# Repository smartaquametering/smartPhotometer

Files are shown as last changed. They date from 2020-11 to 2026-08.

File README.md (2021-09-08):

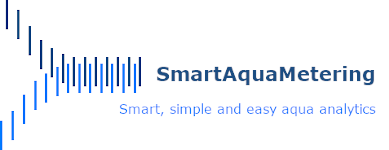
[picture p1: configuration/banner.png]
Banner


# smartPhotoMeter, smartColoriMeter and smartSpectroMeter

Easy-to-use OpenSource devices for **measurement of transmission, emission and absorption of light** at given ranges of wavelengths of colored or not colored substances in solution.

- For analytics of aqueous solutions.
- Works with ultraviolet, visible and near infrared light ranges, by wavelengths around 320 up to 950 nm.

Allows **CIE compliant measurements of colors** and their transformation into various color spaces and color systems including the determination of **colour differences to common color indices/references** according to classic as well as modern standards (ΔE CIE 1976, ΔE CIE 1994, ΔE CIE 2000, ΔE CMC(1:1), ΔE CMC(2:1), ΔE DIN99).

**Turbidity – a source of error**</br>
The turbidity of a sample is often underestimated, because often it is not possible to see it visually.</br>
**The nephelometric turbidity of a sample is measured and displayed for every single measurement automatically.**

Due to their wide range of application, their reliability and robustness

<table>
<tr>
  <td>
  <td>Transmission
  <td>Emission
  <td>Absorbance
  <td>Colorimetric</br>analysis
  <td>Spectral</br>analysis
  <td>Nephelometric</br>turbidity
</tr>
<tr>
  <td><b>smartPhotoMeter</b>
  <td align="center">X
  <td align="center">
  <td align="center">X
  <td align="center">
  <td align="center">
  <td align="center">X
</tr>
<tr>
  <td><b>smartTurbidiMeter</b>
  <td align="center">X
  <td align="center">
  <td align="center">X
  <td align="center">
  <td align="center">
  <td align="center">X
</tr>
<tr>
  <td><b>smartColoriMeter</b>
  <td align="center">
  <td align="center">
  <td align="center">
  <td align="center">X
  <td align="center">
  <td align="center">
</tr>
<tr>
  <td><b>smartSpectroMeter</b>
  <td align="center">X
  <td align="center">X
  <td align="center">X
  <td align="center">X
  <td align="center">X
  <td align="center">X
</tr>
</table>

they **can be perfectly used as portable analytical instruments for outdoor analytics**.

**Your insurance for secure measurement results.**

## Electromagnetic radiation used for photometric and spectrum analysis

In simple terms, photometry is a measurement method for determining the concentration of colored solutions with the aid of electromagnetic radiation (“light”).

The two most common types of photometers are:

- Spectrophotometer
- Filter photometer

In spectrophotometers a monochromator (with prism or with grating) is used to obtain monochromatic light of defined wavelengths. They can also be used to scan the spectrum of the absorbing substance.
Spectrum scans can be used for additional colorimetric analysis at a wavelength range from 360 nm to 830 nm.

In filter photometers, optical filters are used to give the monochromatic light.

### smartPhotoMeter

Due to the evolution and availability of **various types of LEDs** it is easily possible **to obtain nearly monochromatic light with specific wavelength ranges** for respective measurements, but without the need to setup an complex and sensitive monochromator or filter mechanismn.

- The selection of the optimum wavelength range depends on the color of the sample solution and the associated absorption of the complementary color.
- For a blue solution, a wavelength range near to yellow should be used (green LED), while for a yellow solution a blue LED should be used, since always the complementary color is absorbed.
- The more closely the absorption maximum of the substance to be detected is approached, the higher the performance of the photometer will be.
- The smaller the spectral bandwidth of the LED (the range between lower and upper wavelength), the higher the photometer resolution.

### smartTurbidiMeter

The photometric determination of turbidity at a wavelength of 850 nm only to circumvent additional absorption of color in the visible region (following DIN EN ISO 7027).

- Double-beam measurement by using two independant IR light sources and optical paths

### smartColoriMeter

An RGB sensor with **color sensing photodiodes** (red, green, blue) can be used **for colorimetric analysis**.

An IR blocking filter, integrated on-chip and localized to the color sensing photodiodes, minimizes the IR spectral component of the incoming light and allows color measurements to be made accurately.

### smartSpectroMeter

Due to the evolution and availability of **various types of spectral sensors** it is easily possible **to measure the intensity of light at a specific wavelength range**, but without the need to setup an complex and sensitive monochromator or filter mechanismn.

By using a low-voltage **quartz halogen capsule lamp** (Quartz-UV Open) and an **array of spectral sensors** a spectrum for the range of UVA, VIS and IR-A light can be obtained accurately.

These spectral sensors have **20 independent on-device optical filters** whose spectral response is defined in a range **from 330 nm to 940 nm** with a Full Width Half
Max (FWHM) of 20 nm.

Spectrum scans can be used **for qualitative, quantitative and colorimetric analysis** at a wavelength range from 360 nm to 830 nm.

### Cuvette

The selection of an appropriate cuvette for each measurement is crucial. The material (depending on the wavelength) and size of the cuvette are the two key factors.

- High-quality materials such as quartz are used in rectangular standard cuvettes for measurements in the UV range.
- In addition to round and rectangular cuvettes, there are also special cuvettes, such as flow-through cuvettes, where the sample solution is passed into and out of the cuvette by a pump.
- The size of the cuvette is directly related to the layer thickness that is effective in the Lambert-Beer law. Generally speaking, the larger the cuvette and the sample volume, the greater the layer thickness, and the more sensitive the measurement can be.

### Setup options

<table>
<tr>
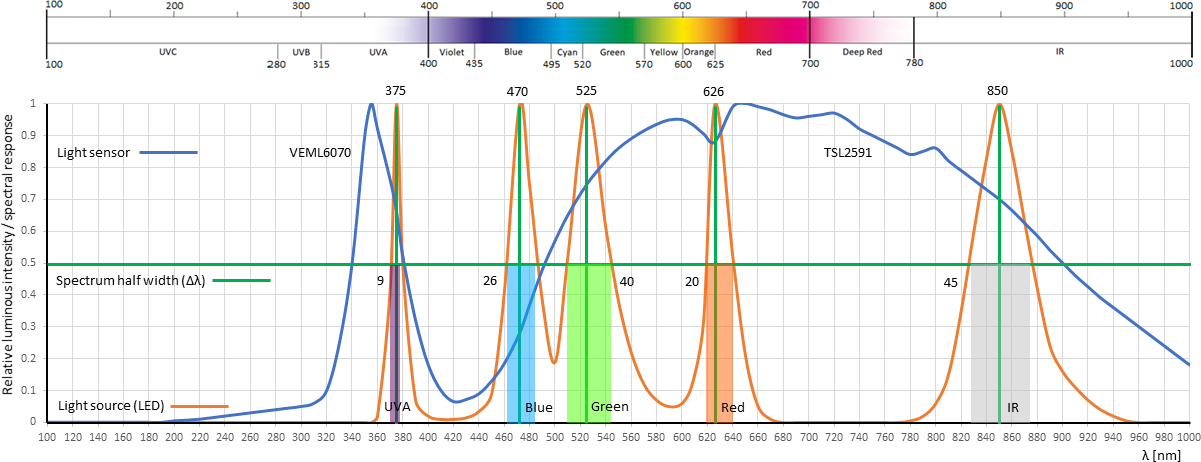
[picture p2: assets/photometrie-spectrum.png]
Photometrie spectrum
  <td colspan=6 align="center">
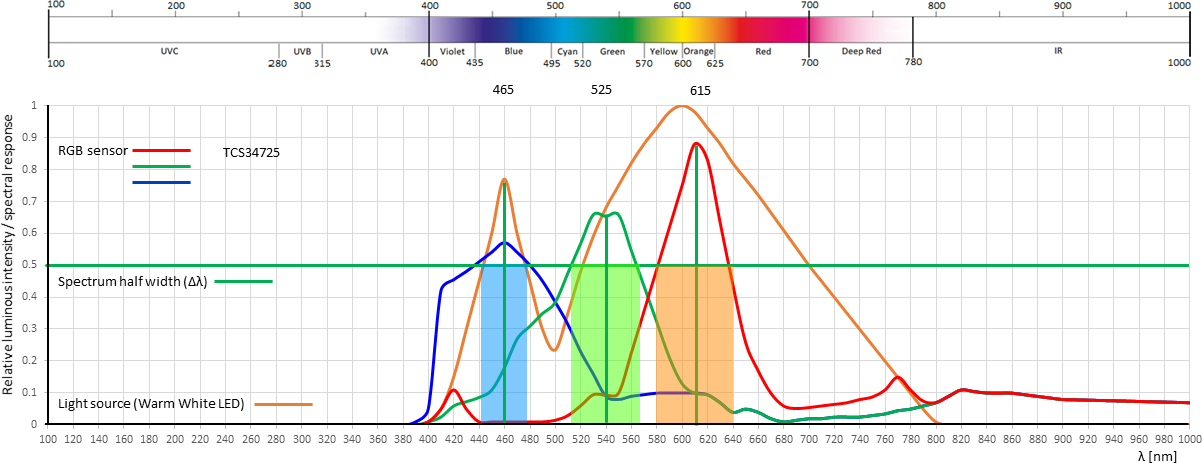
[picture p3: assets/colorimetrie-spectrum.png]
Colorimetriemetrie spectrum
                               
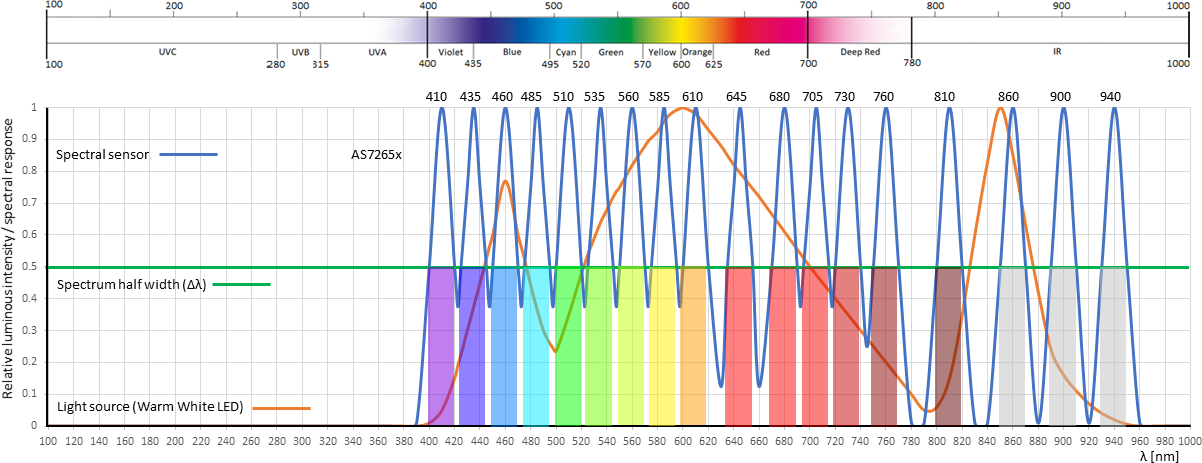
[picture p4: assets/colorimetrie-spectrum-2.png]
Colorimetriemetrie spectrum
                               
</tr>
<tr>
  <td colspan=6><sub><b>Ultraviolet radiation</b>
</tr>
<tr>
  <td>
  <td><sub>100-280 nm
  <td colspan=2><sub>UVC
  <td rowspan=2><sub>UV transmitting quartz glass cuvette</br>> 190 nm
  <td rowspan=3><sub>Numerous anorganic and</br>especially organic compounds</br>absorb UV light
</tr>
<tr>
  <td>
  <td><sub>280-315 nm
  <td colspan=2><sub>UVB
</tr>
<tr>
  <td>
  <td><sub>315-400 nm
  <td colspan=2><sub>UVA
  <td><sub>Borosilicate glass cuvette</br>> 290 nm
</tr>
<tr>
  <td colspan=6><sub><b>Colors of light and complementary colors</b>
</tr>
<tr>
  <td>
  <td><sub>400–435 nm
  <td><sub>Violet
  <td><sub>Yellow-Green
  <td rowspan=8><sub>Normal glass (soda-lime glass) cuvette</br>> 350 nm
  <td rowspan=8><sub>Anorganic compounds</br>by using calibrated test
</tr>
<tr>
  <td>
  <td><sub>435–495 nm
  <td><sub>Blue
  <td><sub>Yellow
</tr>
<tr>
  <td>
  <td><sub>495–520 nm
  <td><sub>Cyan (Blue-Green)
  <td><sub>Red
</tr>
<tr>
  <td>
  <td><sub>520–570 nm
  <td><sub>Green
  <td><sub>Violet
</tr>
<tr>
  <td>
  <td><sub>570–600 nm
  <td><sub>Yellow
  <td><sub>Blue
</tr>
<tr>
  <td>
  <td><sub>600–625 nm
  <td><sub>Orange
  <td><sub>Cyan (Blue-Green)
</tr>
<tr>
  <td>
  <td><sub>625–700 nm
  <td><sub>Red
  <td><sub>Cyan (Blue-Green)
</tr>
<tr>
  <td>
  <td><sub>700–780 nm
  <td><sub>Deep Red
  <td><sub>Cyan (Blue-Green)
</tr>
<tr>
  <td colspan=6><sub><b>Infrared radiation</b>
</tr>
<tr>
  <td>
  <td><sub>780-1400 nm
  <td colspan=2><sub>IR-A (NIR)
  <td rowspan=3><sub>
	  <td rowspan=3><sub>Nephelometric turbidity measurement</br>Biological samples</br>Sectroscopic analysis of aqueous solutions
</tr>
<tr>
  <td>
  <td><sub>1400-3000 nm
  <td colspan=2><sub>IR-B (SWIR)
</tr>
<tr>
  <td>
  <td><sub>3000 nm - 1 mm
  <td colspan=2><sub>IR-C (MWIR, LWIR, FIR)
</tr>
</table>

## Reducing complexity
- by using low-voltage **RGB, UVA and IR-A LEDs** and **quartz halogen capsule lamps** (Quartz-UV Open).
- by the integration of various **digital light and spectral sensors orchestrated by simple microcontrollers**.
- by distributing different analysis methods **on multiple meshed devices**.
- by the strict **segregation of data acquisition, processing, transmission, analytics and their visualisation** on different layers and devices.

## Being Smart - The difference
Connect all devices (Microcontroller including their connected LED/Halogen fireworks and light sensors) via WiFi to your internal network and orchestrate them by using simple web- or MQTT-based APIs.

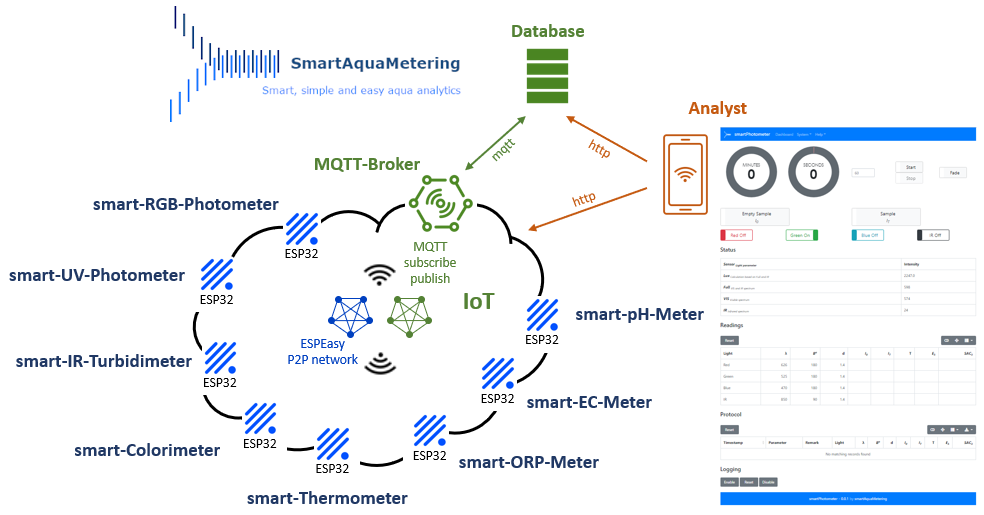
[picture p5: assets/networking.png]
Networking


Any device (e.g. PC, Laptop, Tablet, smartPhone, ...) with a standard web browser can be used to access a simple web page on the microcontroller (MC).

A Javascript application will start within your browser and is triggering and managing all analytis, evaluation of measured values and their visualisation.

### Environmental monitoring
Monitor and secure your environment in real time with online monitoring by logging readings into a central database with MQTT-based APIs.

### Absorbance measurement

The principle of absorption photometers is that (as far as possible) monochromatic light is allowed to pass through a cuvette containing the solution. It then reaches a light sensor, that measures the intensity of the light compared to the intensity after passing through an identical cuvette with the same solvent but without the colored substance. From the ratio between the light intensities, knowing the capacity of the colored substance to absorb light, it is possible to calculate the concentration of the substance using Lambert-Beer's law.

<table>
  <tr>
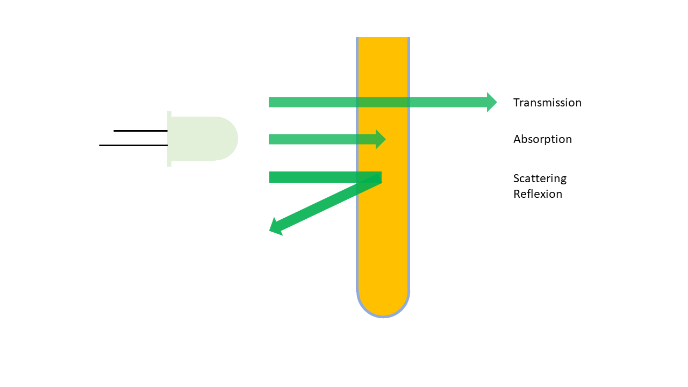
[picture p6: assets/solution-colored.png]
Colored solution
    <td>
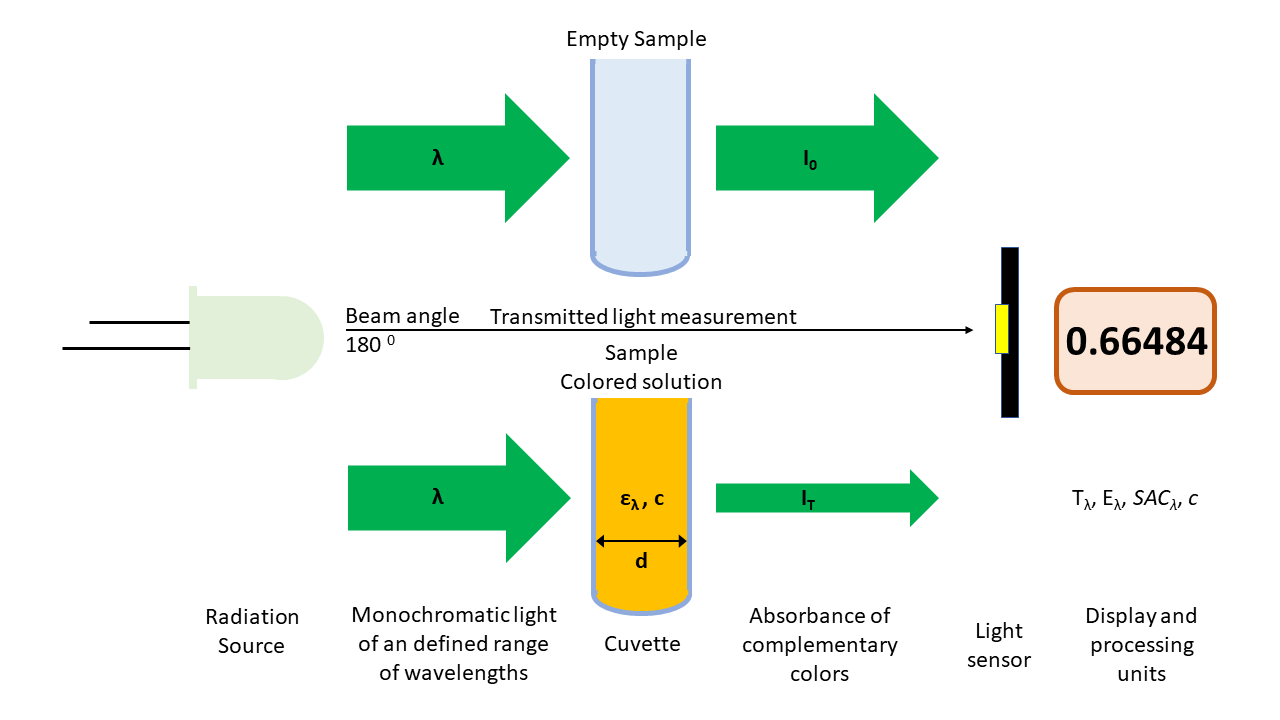
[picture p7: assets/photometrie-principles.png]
Principles of photometrie
    <td>
  </tr>
<tr>
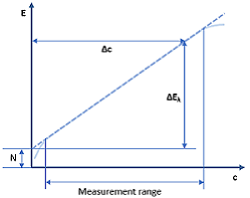
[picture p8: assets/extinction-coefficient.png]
Extinction coefficient
  <td>
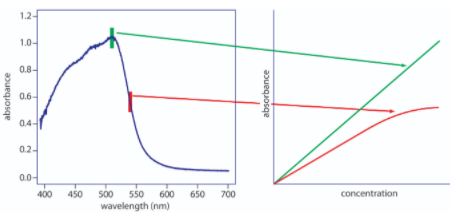
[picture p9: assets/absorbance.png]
Absorbance
  <td>
</tr>
<tr>
<td><sub>λ</td>
<td><sub>Wavelength [nm]</td>
</tr>
<tr>
<td><sub><var>B<sup>o</sup></var></td>
<td><sub>
	Beam (measuring) angle [<var><sup>o</sup></var>]</br>
	<var>180 <sup>o</sup>: Transmitted light measurement (Absorbance)</var></br>
	<var>90 <sup>o</sup>: Nephelometric turbidity (scattered light) measurement</var>
</td>
</tr>
<tr>
  <td><sub><var>I<sub>0</sub></var></td>
  <td><sub>Intensity of incident light [lux]</td>
</tr>
<tr>
<td><sub><var>I<sub>T</sub></var></td>
<td><sub>Intensity of transmitted light [lux]</td>
</tr>
<tr>
<td><sub>T = <var>I<sub>T</sub></var> / <var>I<sub>0</sub></var></td>
<td><sub>
	Transmission</br>
	Energy passing through</br>
	Range: 0.0 - 1.0
</td>
</tr>
<tr>
<td><sub>A = 1 - T</td>
<td><sub>
	Absorption</br>
	Energy lost
</td>
</tr>
<tr>
<td><sub><var>E<sub>λ</sub></var> = - log ( T ) = log ( 1 / T ) = <var>ε<sub>λ</sub></var> * c * d</td>
<td><sub>
	Absorbance</br>
	Attenuation</br>
	Lambert-Beer law</br>
	Optimum range: 0.1 – 1.0
</td>
</tr>
<tr>
<td><sub><var>SAC<sub>λ</sub></var> = <var>E<sub>λ</sub></var> / d * 100</td>
<td><sub>Spectral Absorption Coefficient [<var>m<sup>-1</sup></var>]</td>
</tr>
<tr>
<td><sub>c = <var>E<sub>λ</sub></var> / ( <var>ε<sub>λ</sub></var> * d ) = <var>E<sub>λ</sub></var> * F = <var>E<sub>λ</sub></var> / m</td>
<td><sub>Concentration of absorbing substance in the liquid [mol/l]</td>
</tr>
<tr>
<td><sub>F = 1 / m = 1 / ( <var>ε<sub>λ</sub></var> * d )</td>
<td><sub>
	Factor</br>
	Test specific
</td>
</tr>
<tr>
<td><sub>m = ΔE / Δc = <var>ε<sub>λ</sub></var> * d 
</td>
<td><sub>
   Slope
</td>
</tr>
<tr>
<td><sub>N</td>
<td><sub>
   Zero value
</td>
</tr>
<tr>
<td><sub><var>ε<sub>λ</sub></var></td>
<td><sub>Molar decadic extinction coefficient [l/mol/cm]</td>
</tr>
<tr>
<td><sub>d</td>
<td><sub>Thickness of the solution layer [cm]</td>
</tr>
</table>

### NTU check

- Safely spot interfering turbidities
- Unique for maximum measurement result safety
- Runs automatically with each measurement

### Color measurement

Color assessment focusses on the optical characteristics of the material, i.e. its ability to modify incident light waves.
If an object is exposed to light, it reflects a certain portion of the light, absorbs another portion and transmits the rest.

- *Reflectance* is the basic value for color measurement at reflecting materials (surfaces).
- *Transmittance* is the basic value for color measurement at transparent materials (clear liquids, foils).

Color perception is, like any other spatial perception, three-dimensional. This means that colors can be described by three clear measures of quantity like e.g. lightness, hue and saturation.

CIE 1931 is a Color Matching System that specify a measured color numerically by 3 functions called the RGB color matching functions.

Color Matching functions have three fixed primary colors and each function outputs the amount of primary needed to create a desired color when all three are mixed.
700nm, 546.1nm and 435.8nm are the primaries of the 1931 RGB color matching functions: r(λ), g(λ), b(λ). Plotted below.

Die Werte X, Y und Z werden Normfarbwerte oder auch Tristimulus-Werte genannt. 

A colorimeter is generally any tool that characterizes color samples to provide an objective measure of color characteristics.

Color parameters:
- Conversions of measured color into various color spaces
- Measuring of color distance/difference against quality control standards (e.g. color scales/indices/references)

#### Color Spaces

Normally, color spaces are three dimensional spaces with a color component on every axis. The colour of an object is defined by combining these three elements.

The following color spaces are supported:

<table>
<tr>
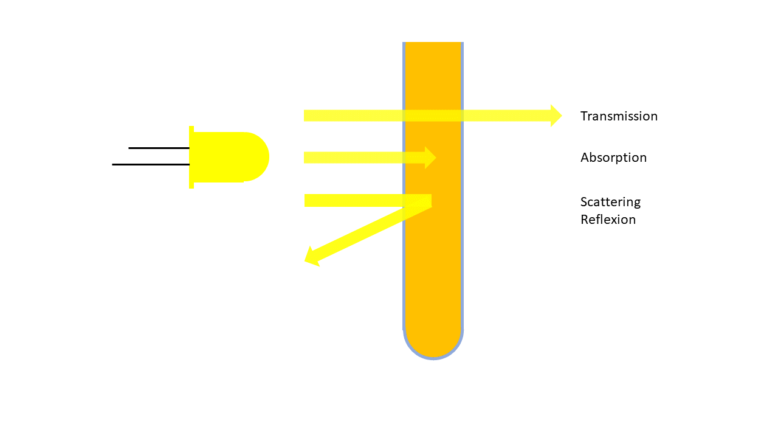
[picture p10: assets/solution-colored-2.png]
Colored solution
    <td>
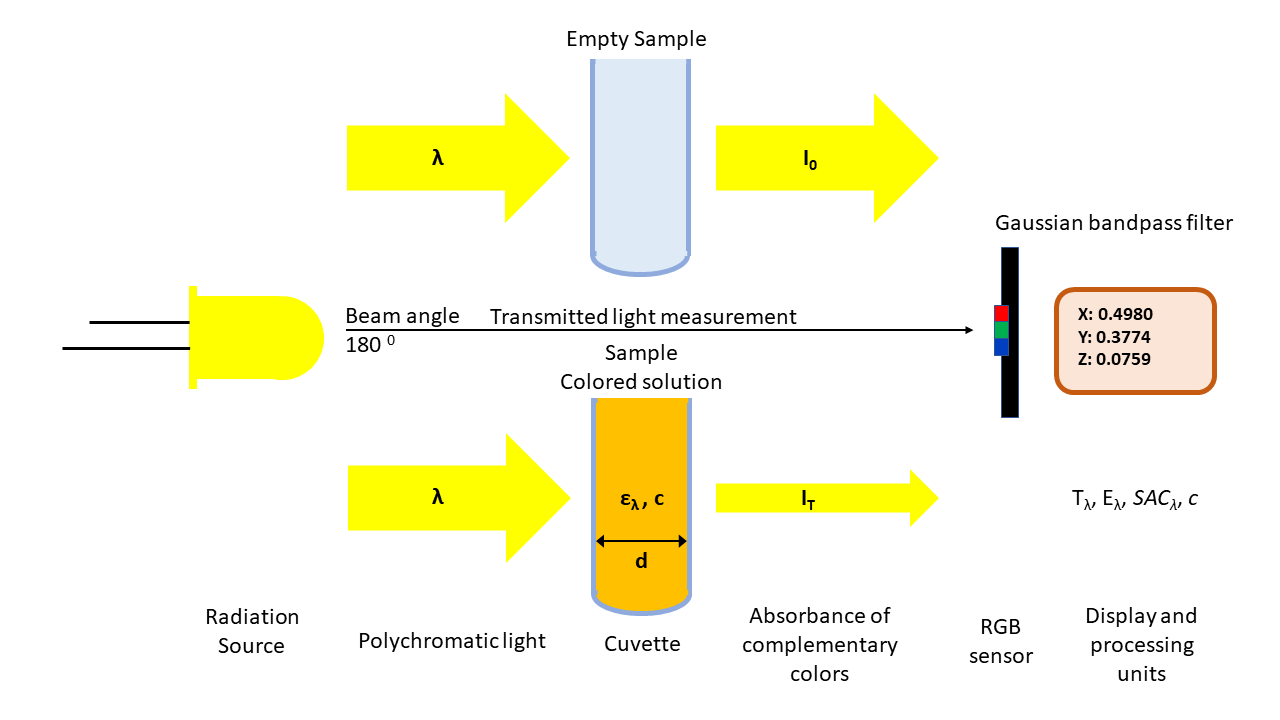
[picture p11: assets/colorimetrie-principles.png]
Principles of colorimetrie
    <td>
</tr>
<tr>
  <td>Extinction coefficient
  <td>Absorbance
</tr>
<tr>
<td><sub>Φ</td>
<td><sub>Luminous flux [lm]</td>
</tr>
<tr>
<td><sub>Ω</td>
<td><sub>Solid angel in Steradian [sr]</td>
</tr>
<tr>
<td><sub>E = Φ / A</td>
<td><sub>Illumination [lux] [lm / <var>m<sup>2</sup></var>]</td>
</tr>
<tr>
<td><sub>I = Φ / Ω</td>
<td><sub>Luminous intensity or candelpower [mcd] [lm / sr]</td>
</tr>
<tr>
<td><sub></td>
<td><sub>Clear (unfiltered) value</td>
</tr>
<tr>
<td><sub>
RGB are tristimulus values</br>
r = R/(R+G+B)</br>
g = G/(R+G+B)</br>
b = B/(R+G+B)</br>
rgb are chromaticity coordinates and r + g + b = 1</td>
<td><sub>R, G and B (filtered) values</td>
</tr>
<tr>
<td><sub>X = a * Tx + b * Tz</br>
Y = Ty = Illuminance</br>
Z = c * Tz</br>
</br>
a, b and c depend on illuminant and observer</br>
Standard illuminant C and 2°-observer</td>
<td><sub>Standard tristimulus values</br>
CIE-1931 color space (tristimulus system)</td>
</tr>
<tr>
<td><sub>x = X / ( X + Y + Z )</br>
y = Y / ( X + Y + Z )</br>
z = Z / ( X + Y + Z )</br>
x + y + z = 1</td>
<td><sub>Chromaticity coordinates in the tristimulus system</td>
</tr>
<tr>
<td><sub><var>T<sub>C</sub></var> = 449 * <var>n<sup>3</sup></var> + 3525 * <var>n<sup>2</sup></var>  + 6823.3 * n + 5520.33</br>
where n = ( x − 0.3320 ) / ( 0.1858 − y )</td>
<td><sub>Light color temperature (CCT) in Kelvin [<var><sup>o</sup></var>K]</br>
McCamy’s formula</td>
</tr>
<tr>
<td><sub>L* = 116 * ∛( Y / <var>Y<sub>n</sub></var> ) - 16</br>
a* = 500 * ( ∛( X / <var>X<sub>n</sub></var> ) - ∛( Y / <var>Y<sub>n</sub></var> ) )</br>
b* = 200 * ( ∛( Y / <var>Y<sub>n</sub></var> ) - ∛( Z / <var>Z<sub>n</sub></var> ) )</br>
C* = √( <var>a*<sup>2</sup></var> + <var>b*<sup>2</sup></var> )</br>
<var>h<sub>ab</sub></var> = arctan( b* / a* )</br>
</br>
<var>X<sub>n</sub></var>, <var>Y<sub>n</sub></var> and <var>Z<sub>n</sub></var> depend on illuminant and observer</td>
<td><sub>CIE-L*a*b* colorimetric system</td>
</tr>
<tr>
<td><sub>Calculated from standard tristimulus values X, Y and Z, but with different equations</br>
The color space is related to the CIE-Lab space in purpose, but differs in implementation</td>
<td><sub>Hunter-Lab-values</br>
Used for the assessment of surface colors</td>
</tr>
</table>

#### Color Distance

To determine color differences according to classic as well as modern standards (ΔE CIE 1976, ΔE CIE 1994, ΔE CIE 2000, ΔE CMC(1:1), ΔE CMC(2:1), ΔE DIN99).

<table>
<tr>
<td><sub>ΔE*</br>
</br>
ΔE*wp: Color difference between the sample and water</br>
ΔE*ws: Color difference between the standard solution and water</br>
</br>
ΔE*wp < ΔE*ws
</td>
<td><sub>CIE-L*a*b* difference values</td>
</tr>
</table>

#### Color Scales

Color scales/indices/references are common and simple methods to determine the color of a sample.

The sample is compared with a series of colored standards/references. The result corresponds to the standard with the most similar colors.

<table>
<tr>
<td><sub><b>Color scale</b></td>
<td><sub><b>Range</b></td>
<td><sub><b>Calibration / Standard</b></td>
<td><sub><b>Measurement</b></td>
</tr>
<tr>
<td><sub>Iodine Color Number</td>
<td><sub>0 - 120</td>
<td><sub>mg of iodine per 100ml potassium iodide solution (DIN 6162)</td>
<td><sub></td>
</tr>
<tr>
<td><sub>Hazen Color Number (APHA)</td>
<td><sub>0 - 1000</td>
<td><sub>Measure yellow hues in liquids (DIN ISO 6271)</br>
</br>
Calibration standard with 500 mg/l Pt/Co 500 (500 Hazen)</td>
<td><sub><var>E<sub>430</sub></var> = 0.115</br>
<var>E<sub>455</sub></var> = 0.135</br>
<var>E<sub>480</sub></var> = 0.115</br>
<var>E<sub>510</sub></var> = 0.06</br>
</br>
(Optical path length: 10 mm)</td>
</tr>
<tr>
<td><sub>Gardner Color Number</td>
<td><sub>0 - 18</td>
<td><sub></td>
<td><sub></td>
</tr>
<tr>
<td><sub>Lovibond Color System</td>
<td><sub>Lovibond® 1)
yellow/red Ly 0 - 120, Lr 0 - 20</td>
<td><sub></td>
<td><sub></td>
</tr>
<tr>
<td><sub>European Pharmacopoeia (EP) Color Determination</td>
<td><sub>B, BY, Y, GY, R</td>
<td><sub>Colors in CIE-L*a*b* colorimetric system</td>
<td><sub></td>
</tr>
<tr>
<td><sub>US Pharmacopoeia (USP) Color Determination</td>
<td><sub>A - T</td>
<td><sub>Colors in CIE-L*a*b* colorimetric system</td>
<td><sub></td>
</tr>
<tr>
<td><sub>Chinese Pharmacopoeia (CP) Color Determination</td>
<td><sub>OR,OY,Y,YG,BR</td>
<td><sub>Colors in CIE-L*a*b* colorimetric system</td>
<td><sub></td>
</tr>	
<tr>
<td><sub>Klett Color Number</td>
<td><sub>0 - 1000</td>
<td><sub>Absorption of a sample liquid in a square cuvette of 4cm (or 2cm) path length measured through a blue filter</td>
<td><sub><var>Klett<sub>Phot</sub></var> = <var>E<sub>470</sub></var></td>
</tr>
<tr>
<td><sub>Hess-Ives Color Number</td>
<td><sub></td>
<td><sub>Cosmetic industry, color evaluation of fat derivatives</br>
</br>
R, G and B are the color components for the red (640 nm), green (560nm) and blue (464nm) shares</td>
<td><sub>H-I = (R + G + B) * 6 / layerthickness</br>
R = 43,45 * <var>E<sub>640</sub></var></br>
G = 162,38 * <var>E<sub>560</sub></var></br>
B = 22,89 * ( <var>E<sub>460</sub></var> + <var>E<sub>470</sub></var> ) / 2</td>
</tr>
<tr>
<td><sub>Yellowness Index</br>
(ASTM D1925)</td>
<td><sub></td>
<td><sub>For transparent liquids on the basis of CIE XYZ-tristimulus values, standard illuminant C and the 2°-standard observer.</td>
<td><sub>Yi = 100 * ( Tx - Tz / Ty )</td>
</tr>
<tr>
<td><sub>ADMI Color Number</td>
<td><sub>0 - 500</td>
<td><sub>Colors in CIE-L*a*b* colorimetric system</td>
<td><sub></td>
</tr>
<tr>
<td><sub>Acid Wash Color Determination</td>
<td><sub>1 - 14</td>
<td><sub>Colors in CIE-L*a*b* colorimetric system</td>
<td><sub></td>
</tr>
<tr>
<td><sub>EBC Brewery Color Number</td>
<td><sub></td>
<td><sub>Optical path length: 10 mm</td>
<td><sub>25 * <var>E<sub>430</sub></var></td>
</tr>
<tr>
<td><sub>ASBC Brewery Color Number</td>
<td><sub></td>
<td><sub>1 ASBC = 0.375 EBC color + 0.46</td>
<td><sub>12.7 * <var>E<sub>430</sub></var></td>
</tr>
<tr>
<td><sub><var>SAC<sub>436</sub></var></td>
<td><sub></td>
<td><sub>Spectral Absorption Coefficient describes the yellow colouring of potable-, used- or wastewater. The measuring range is indicated in m-1.
(Extinction per meter optical path lenght [Ext/m]).</td>
<td><sub><var>E<sub>436</sub></var></td>
</tr>
</table>

##### European Pharmacopoeia (EP) color scales in CIE-L*a*b* colorimetric system (C°2, d=5cm)
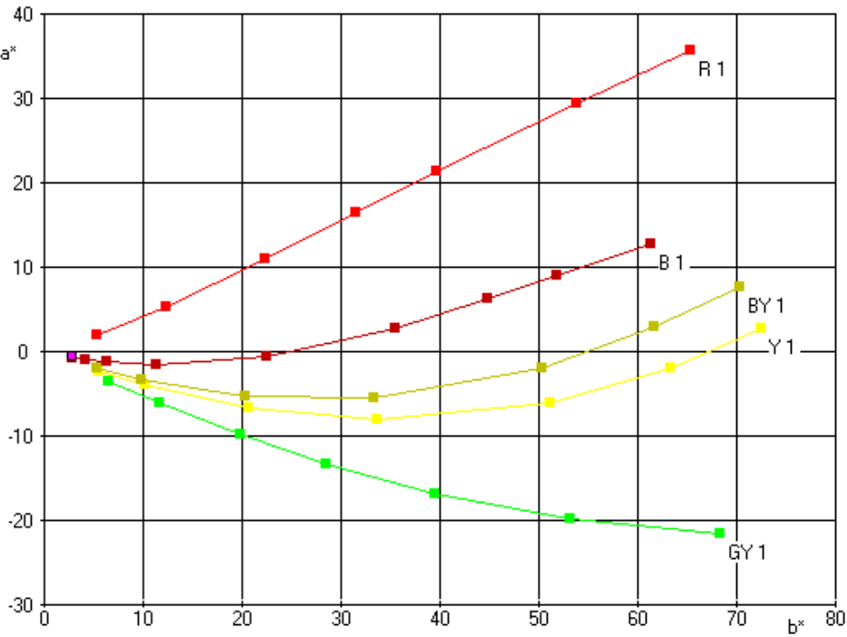
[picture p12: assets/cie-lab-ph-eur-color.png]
European Pharmacopoeia (EP) color scales in CIE-L*a*b* colorimetric system


##### US Pharmacopoeia (USP) color scales in CIE-L*a*b* colorimetric system (C°2, d=5cm)
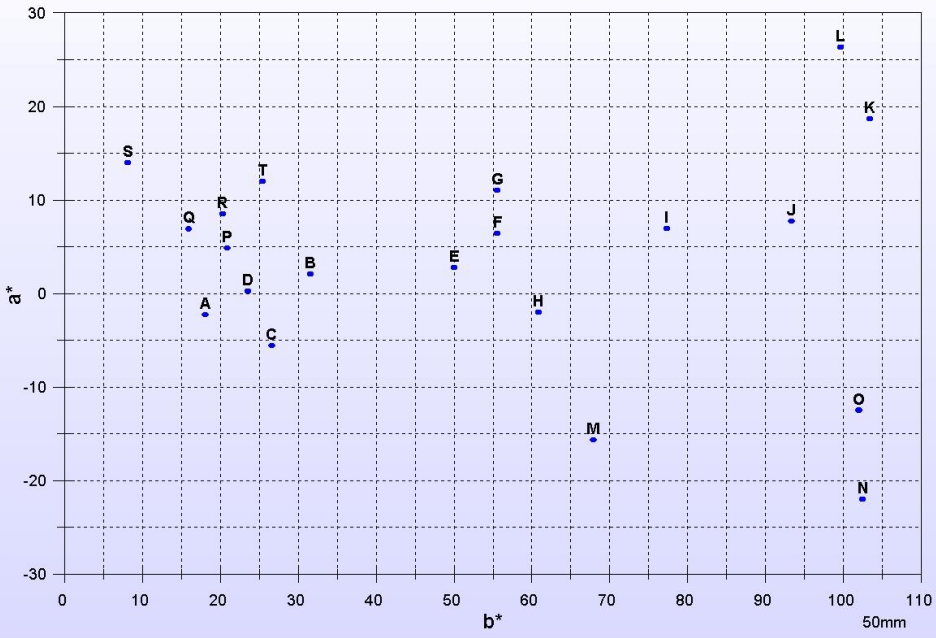
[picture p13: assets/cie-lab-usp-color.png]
US Pharmacopoeia (USP) color scales in CIE-L*a*b* colorimetric system


##### Chinese Pharmacopoeia (CP) color scales in CIE-L*a*b* colorimetric system (C°2, d=5cm)
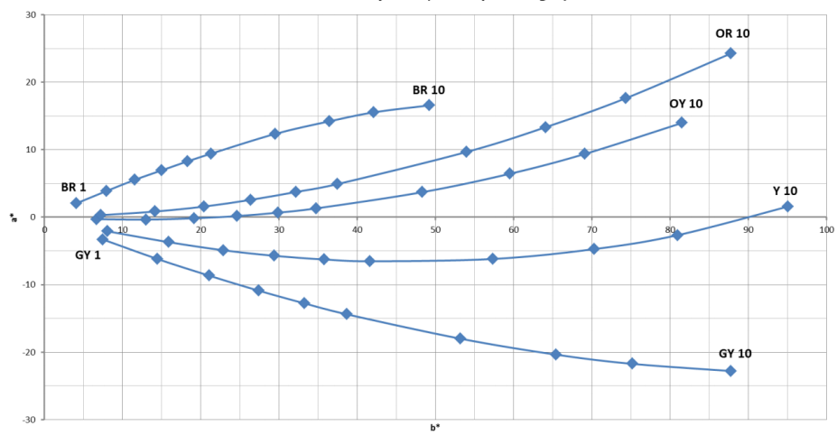
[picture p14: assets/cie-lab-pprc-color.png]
Chinese Pharmacopoeia (CP) color scales in CIE-L*a*b* colorimetric system


##### Acid Wash color scales in CIE-L*a*b* colorimetric system (C°2, d=5cm)
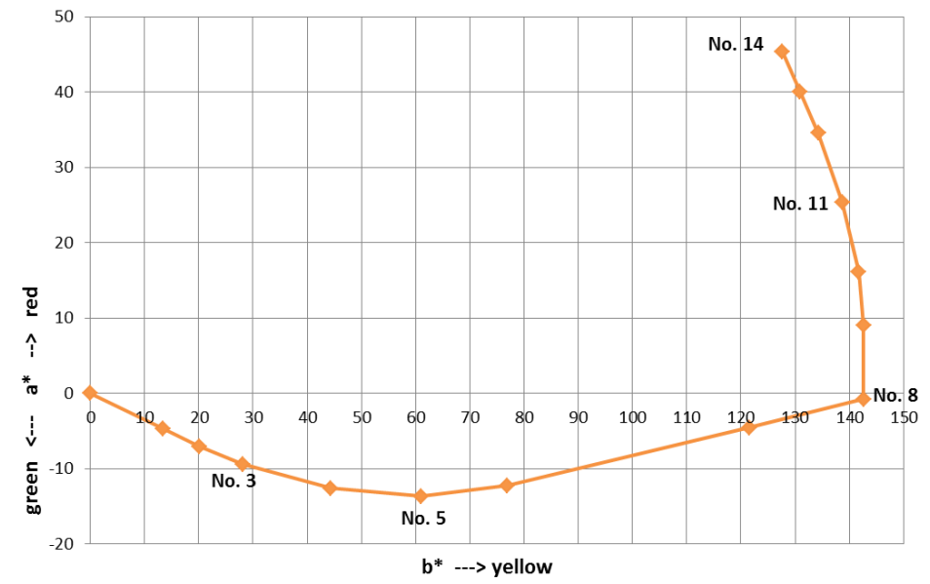
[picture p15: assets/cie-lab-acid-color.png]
Acid Wash color scales in CIE-L*a*b* colorimetric system


##### Comparison of ASTM D1500 and ASTM D156 (Saybolt) color
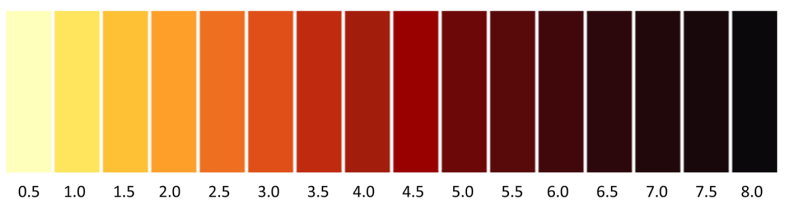
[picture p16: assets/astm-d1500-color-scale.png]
ASTM D1500 color scale

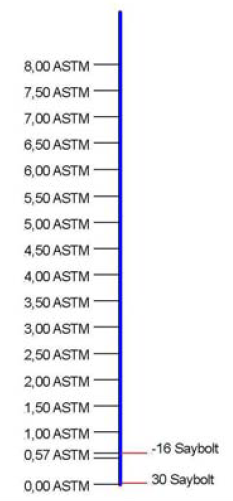
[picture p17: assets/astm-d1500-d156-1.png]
Comparison of ASTM D1500 and ASTM D156 (Saybolt) color

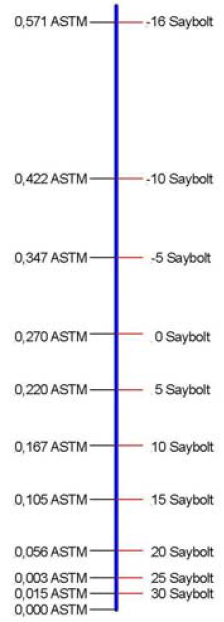
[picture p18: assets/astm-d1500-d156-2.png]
Comparison of ASTM D1500 and ASTM D156 (Saybolt) color


##### Comparison of visual color systems with the Z-transmittances (C°2, d=1cm)
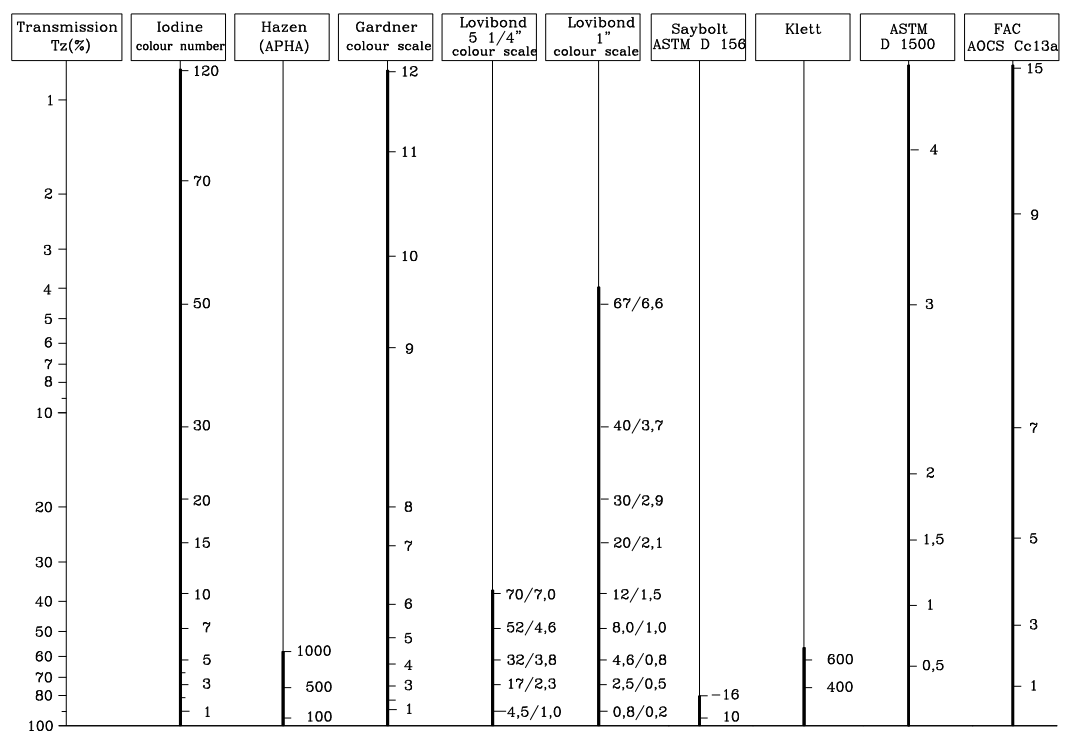
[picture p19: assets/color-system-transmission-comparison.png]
Comparison of visual color systems with the Z-transmittances


##### Iodine color number (C°2, d=1cm)
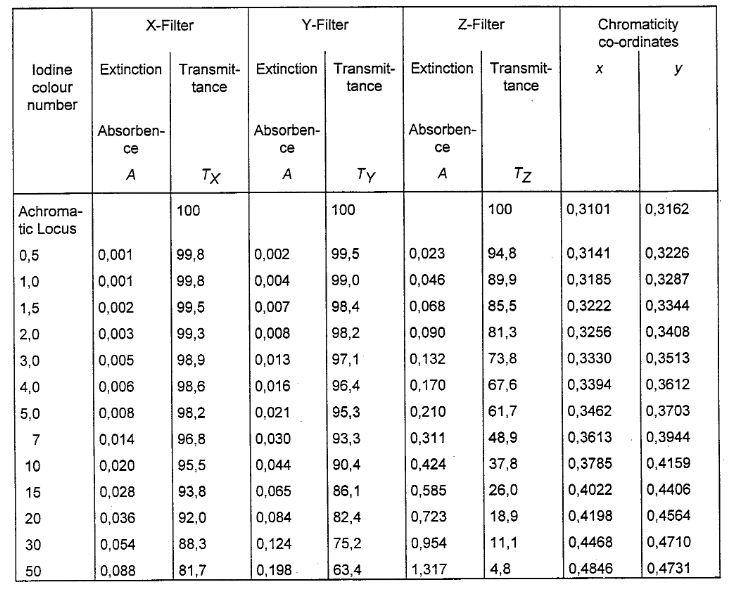
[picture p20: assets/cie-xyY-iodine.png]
Iodine color number (C°2, d=1cm)


##### Hazen number (C°2, measured with d=5cm, calculated to d=1cm)
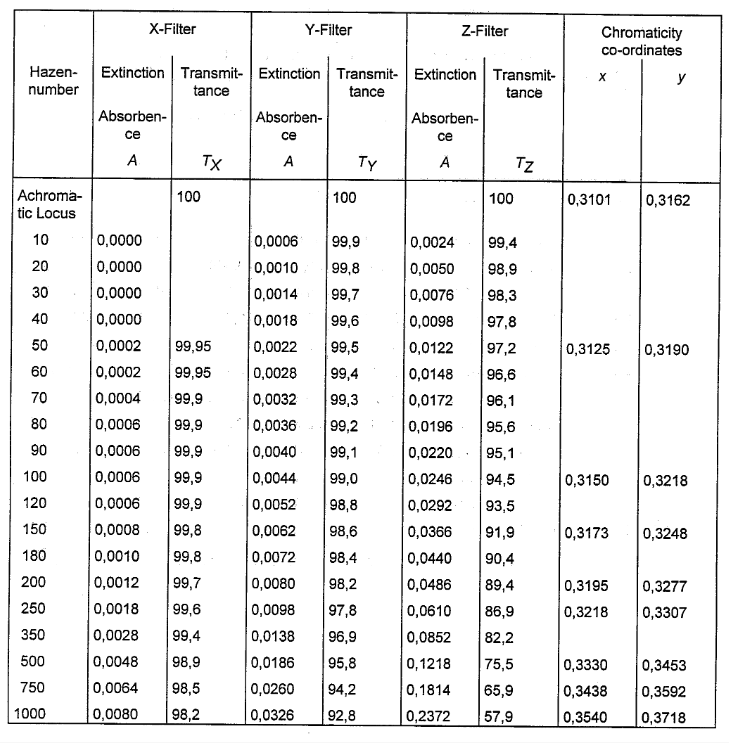
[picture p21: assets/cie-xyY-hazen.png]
Hazen number (C°2, measured with d=5cm, calculated to d=1cm)


##### Gardner color scale (C°2, d=1cm)
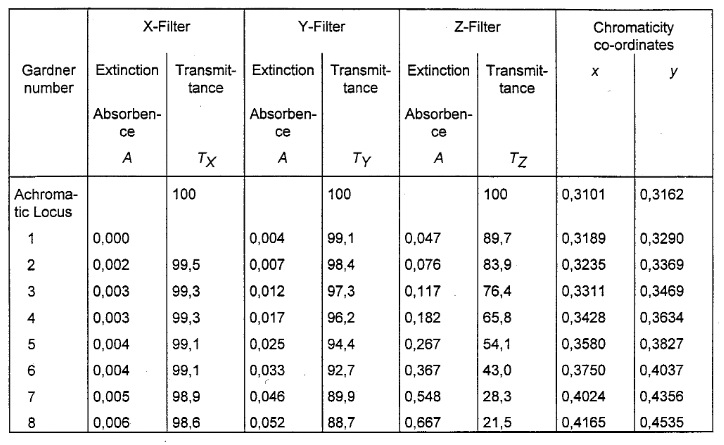
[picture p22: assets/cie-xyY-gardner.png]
Gardner color scale (C°2, d=1cm)


##### Iodine, Hazen and Gardner color scales in CIE-L*a*b* colorimetric system (C°2, d=1cm)
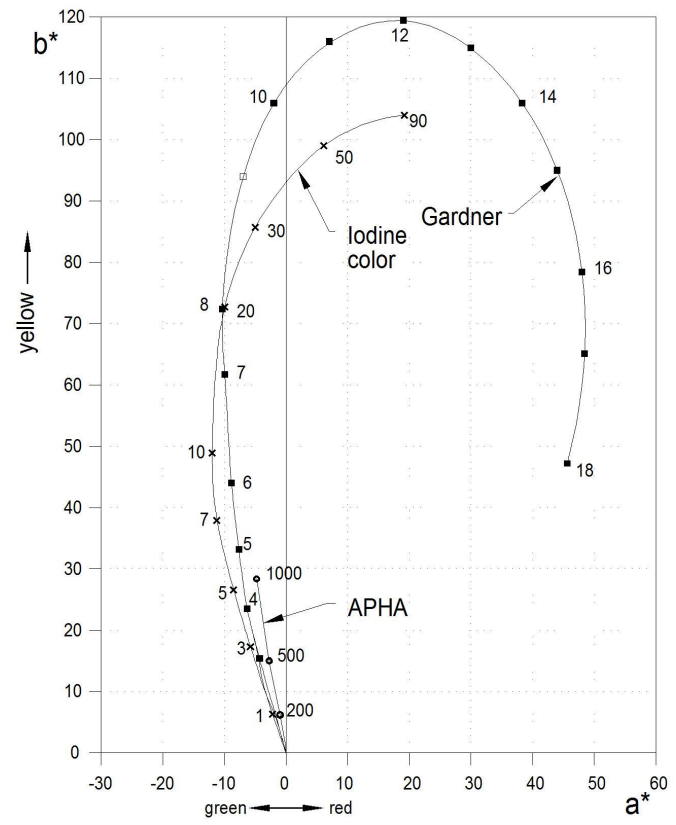
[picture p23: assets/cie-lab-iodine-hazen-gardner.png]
Iodine, Hazen and Gardner color scales in CIE-L*a*b* colorimetric system (C°2, d=1cm)


##### ADMI and Hazen color scales in CIE-L*a*b* colorimetric system (C°2, d=1cm)
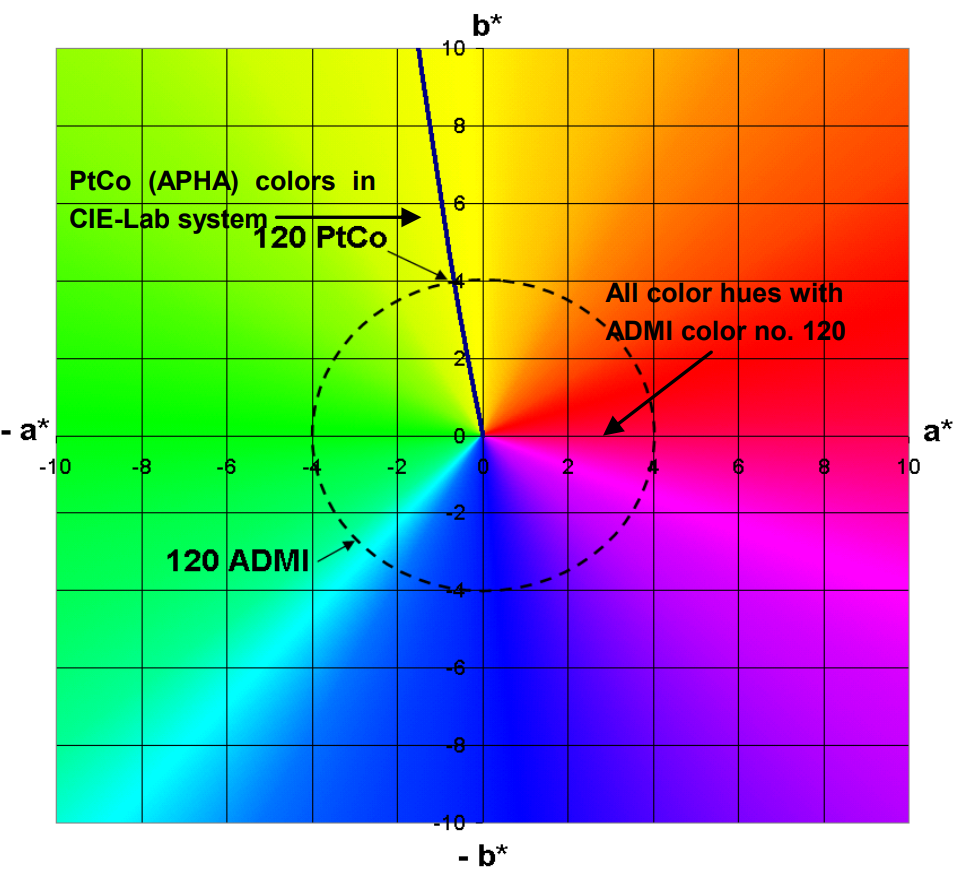
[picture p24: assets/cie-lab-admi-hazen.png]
ADMI and Hazen color scales in CIE-L*a*b* colorimetric system


### Turbidity measurement

Turbidity (opacity, clouding, haze) is an optical property of a liquid sample describing the degree of clarity. Turbidity is caused by small suspended (insoluble) particles having a refractive index different from the medium. This results in absorption, scattering and reflection of the incident light.
In general, the higher the turbidity, the more intense is the resulting scattered light.
Turbidity particles absorb at virtually all frequencies, due to their three-dimensional structure.

Additional absorption of color in the visible region may be circumvented by a measurement in the infrared (IR) or near-infrared (NIR) range.
Accordingly, the attenuation of transmission is a measure of the concentration of turbidity-causing solids.
The photometric determination of turbidity is usually done at a wavelength of 860 nm (DIN EN ISO 7027).

Factors that influence this intensity:
- Wavelength of the incident light
- Particle size and shape
- Refractive index and color of the sample

Photometry is an objective measurement that allows the comparison of different levels of turbidity:

- Double-beam measurement by using two independant IR light sources and optical paths
  - In case of heavy turbidity
    - Absorbance measurement (transmitted light measurement) at a 180° beam angle from 2-400 NTU
  
  Recommended measuring range: 40–4000 FAU (DIN EN ISO 7027) Light source and
detector are located on the same axis (180° angle). The reduced light intensity which
remains after passing through the sample is measured.

  - In case of low turbidity
    - Nephelometric stray light measurement at a 90° beam angle from 0.1-1000 NTU
    The intensity of the light which is scattered by undissolved particles in the sample is measured.
The international unit is the nephelometric turbidity unit, NTU. Other units are FTU (formazine turbidity unit), FNU (formazine nephelometric unit) and TU/F (turbidity unit formazine). 
Recommended measuring range: 0–40 FNU (DIN EN ISO 7027)
The international unit is FAU (formazine attenuation unit). In Germany, the spectral absorption coefficient SAK [1/m] is often used.

· Transmitted light measurement at medium to high turbidity concentration (about
40–4000 FAU); used e.g. for determination of the solid portion in activated sludge.
· Light scattering measurement at low turbidity concentration (about 1–40 FNU); e.g. in
treated wastewater.

<table>
  <tr>
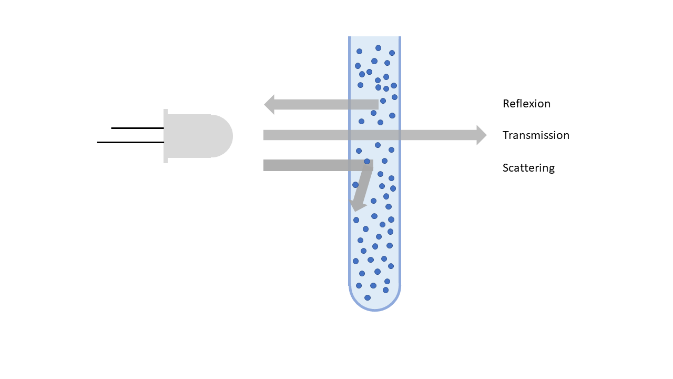
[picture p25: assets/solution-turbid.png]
Turbid solution
    <td>
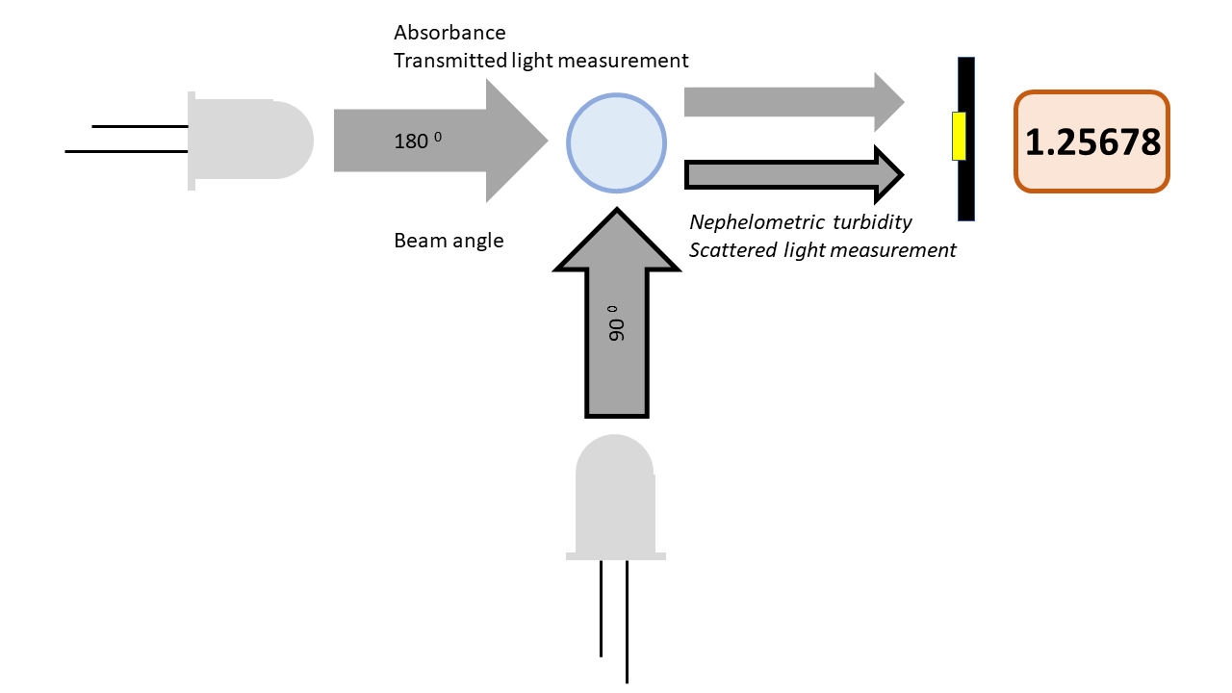
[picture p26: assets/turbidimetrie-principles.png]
Principles of turbidimetrie
    <td>
  </tr>
<tr>
<td><sub>λ</td>
<td><sub>Wavelength [nm]</td>
</tr>
<tr>
<td><sub><var>B<sup>o</sup></var></td>
<td><sub>
	Beam (measuring) angle [<var><sup>o</sup></var>]</br>
	<var>180 <sup>o</sup>: Transmitted light measurement (Absorbance)</var></br>
	<var>90 <sup>o</sup>: Nephelometric turbidity (scattered light) measurement</var>
</td>
</tr>
<tr>
<td><sub><var>I<sub>0</sub></var></td>
<td><sub>Intensity of incident light [lux]</td>
</tr>
<tr>
<td><sub><var>I<sub>T</sub></var></td>
<td><sub>Intensity of transmitted light [lux]</td>
</tr>
<tr>
<td><sub>T = <var>I<sub>T</sub></var> / <var>I<sub>0</sub></var></td>
<td><sub>
	Transmission</br>
	Energy passing through</br>
	Range: 0.0 - 1.0
</td>
</tr>
<tr>
<td><sub>A = 1 - T</td>
<td><sub>
	Absorption</br>
	Energy lost
</td>
</tr>
<tr>
<td><sub><var>E<sub>λ</sub></var> = - log ( T ) = <var>ε<sub>λ</sub></var> * c * d</td>
<td><sub>
	Absorbance</br>
	Attenuation</br>
	Lambert-Beer law</br>
	Optimum range: 0.1 – 1.0
</td>
</tr>
<tr>
<td><sub><var>SAC<sub>λ</sub></var> = <var>E<sub>λ</sub></var> / d * 100</td>
<td><sub>Spectral Absorption Coefficient [<var>m<sup>-1</sup></var>]</td>
</tr>
<tr>
<td><sub>c = <var>E<sub>λ</sub></var> / ( <var>ε<sub>λ</sub></var> * d ) = <var>E<sub>λ</sub></var> * F</td>
<td><sub>Concentration of absorbing substance in the liquid [mol/l]</td>
</tr>
<tr>
<td><sub>F = 1 / ( <var>ε<sub>λ</sub></var> * d )</td>
<td><sub>
	Factor</br>
	Test specific
</td>
</tr>
<tr>
<td><sub><var>ε<sub>λ</sub></var></td>
<td><sub>Molar decadic extinction coefficient [l/mol/cm]</td>
</tr>
<tr>
<td><sub>d</td>
<td><sub>Thickness of the solution layer [cm]</td>
</tr>
<tr>
<td><sub>Turbidity</td>
<td><sub>Opacity, clouding, haze</td>
</tr>
<tr>
<td><sub>FNU</td>
<td><sub>Formazine Nephelometric Unit</td>
</tr>
<tr>
<td><sub>NTU</td>
<td><sub>Nephelometric Turbidity Unit</td>
</tr>
<tr>
<td><sub>FAU</td>
<td><sub>Formazine Attenuation Unit</td>
</tr>
</table>

smartPhotometer are in this way cheap, robust and easy-to-use, but very flexible and also provide multiple analysis and reporting options which normally are only available in very expensive high end solutions.

Don't reinvent the wheel and **rely on agile open source communities**.

## Tips and tricks

- The filling level of the cuvette must be at least 4 cm due to the beam path of the photometers.
- Turbid samples have to be filtered; turbidity leads to incorrect results.

## Datasheet

<table>
<tr>
  <td colspan=2><sub><b>Measuring modes</b>
  <td><sub><b>UV SAC</b>
  <td><sub><b>Color</b>
  <td colspan=4><sub><b>VIS SAC / Turbidity</b>
  <td colspan=2><sub><b>Turbidity</b>
  <td colspan=2><sub><b>Spectrum SAC / Turbidity</b>
</tr>
<tr>
  <td>
  <td><sub>Target wavelength
  <td><sub>254 nm
  <td><sub>VIS
  <td colspan=3><sub>VIS, 436 nm
  <td><sub>850 nm
  <td><sub>850 nm
  <td><sub>850 nm
  <td><sub>UVA, VIS, 436 nm, NIR
  <td><sub>850 nm
</tr>
<tr>
  <td colspan=14><sub>Light spectrum
</tr>
<tr>
  <td>
  <td><sub>100-400 nm
  <td><sub>UV
  <td><sub>
  <td colspan=4><sub>
  <td colspan=2><sub>
  <td><sub>UVA
  <td><sub>
</tr>
<tr>
  <td>
  <td><sub>400-780 nm
  <td><sub>
  <td><sub>VIS
  <td colspan=3><sub>VIS
  <td><sub>
  <td colspan=2><sub>
  <td><sub>VIS
  <td><sub>
</tr>
<tr>
  <td>
  <td><sub>> 780 nm
  <td><sub>
  <td><sub>
  <td colspan=3><sub>
  <td><sub>IR
  <td><sub>IR
  <td><sub>IR
  <td><sub>NIR
  <td><sub>IR
</tr>
<tr>
  <td colspan=2><sub><b>Device</b>
  <td><sub><b>smart-UV-Photometer</b>
  <td><sub><b>smartColoriMeter</b>
  <td colspan=4><sub><b>smart-PhotoMeter</b>
  <td colspan=2><sub><b>smartTurbidiMeter</b>
  <td colspan=2><sub><b>smartSpectroMeter</b>
</tr>
<tr>
  <td>
  <td><sub>Measurement method
  <td><sub>Absorbance
  <td><sub>Color index
  <td colspan=3><sub>Absorbance
  <td><sub>Nephelometric turbidity
  <td><sub>Absorbance
  <td><sub>Nephelometric turbidity
  <td><sub>Absorbance, Color index
  <td><sub>Nephelometric turbidity
</tr>
<tr>
  <td>
  <td><sub>Beam angle [<sup>o</sup>]
  <td><sub>180
  <td><sub>180
  <td colspan=3><sub>180
  <td><sub>90
  <td><sub>180
  <td><sub>90
  <td><sub>180
  <td><sub>90
</tr>
<tr>
  <td>
  <td><sub>LED(s) and Sensor chip mounting height [mm]
  <td colspan=10><sub>20.0
</tr>
<tr>
  <td colspan=2><sub><b>Readings</b>
  <td>
  <td>
  <td colspan=4>
  <td colspan=2>
  <td colspan=2>
</tr>

<tr>
  <td>
  <td><sub>Illuminance (<var>E<sub>V</sub></var>) [lux = lm/<var>m<sup>2</sup></var>]
  <td><sub>X
  <td>
  <td><sub>X
  <td><sub>X
  <td><sub>X
  <td><sub>X
  <td><sub>X
  <td><sub>X
  <td><sub>X
  <td><sub>X
</tr>
<tr>
  <td>
  <td><sub>Color index
  <td>
  <td><sub>RGB
  <td colspan=4>
  <td colspan=2>
  <td colspan=2>
</tr>
<tr>
  <td>
  <td><sub>Light color temperature (CCT) [<var><sup>o</sup></var>K]
  <td>
  <td><sub>X
  <td colspan=4>
  <td colspan=2>
  <td colspan=2>
</tr>
<tr>
  <td colspan=2><sub><b>LED(s)</b>
  <td><sub><a href='https://www.nichia.co.jp/specification/products/led/NSPU510CS-E.pdf'>NSPU510CS</a>
  <td><sub><a href='https://cdn.luckylight.cn/media/component/data-sheet/504WC2E-W6-3PC.pdf'>504WC2E-W6-3PC</a>
  <td colspan=3><sub><a href='https://cdn-reichelt.de/documents/datenblatt/A500/LL-509RGBC2E-006.pdf'>LL-509RGBC2E-006</a>
  <td><sub><a href='https://cdn-reichelt.de/documents/datenblatt/A501/HIR383C-L289_ENG_TDS.pdf'>HIR383C-L289</a>
  <td colspan=2><sub>2 x <a href='https://cdn-reichelt.de/documents/datenblatt/A501/HIR383C-L289_ENG_TDS.pdf'>HIR383C-L289</a>
  <td><sub><a href='https://www.lighting.philips.de/api/assets/v1/file/PhilipsLighting/content/fp923874510103-pss-de_de/923874510103_EU.de_DE.PROF.FP.pdf'>7387 10W G4 6V 1CT/10X10F</a>
  <td><sub><a href='https://cdn-reichelt.de/documents/datenblatt/A501/HIR383C-L289_ENG_TDS.pdf'>HIR383C-L289</a>
</tr>
<tr>
  <td>
  <td><sub>Light color
  <td><sub>UVA
  <td><sub>Warm White
  <td><sub>Red
  <td><sub>Green
  <td><sub>Blue
  <td><sub>IR
  <td><sub>IR
  <td><sub>IR
  <td><sub>Warm White
  <td><sub>IR
</tr>
<tr>
  <td>
  <td><sub>Color Rendering Index (CRI) [Ra]
  <td><sub>
  <td><sub>80
  <td><sub>
  <td><sub>
  <td><sub>
  <td><sub>
  <td><sub>
  <td><sub>
  <td><sub>100
  <td><sub>
</tr>
<tr>
  <td>
  <td><sub>Light color temperature (CCT) [<var><sup>o</sup></var>K]
  <td><sub>
  <td><sub>3000
  <td><sub>
  <td><sub>
  <td><sub>
  <td><sub>
  <td><sub>
  <td><sub>
  <td><sub>3200
  <td><sub>
</tr>
<tr>
  <td>
  <td><sub>Standard illuminant (CIE 1931/<var>2<sup>o</sup></var>)
  <td><sub>
  <td><sub>LED-B2
  <td><sub>
  <td><sub>
  <td><sub>
  <td><sub>
  <td><sub>
  <td><sub>
  <td><sub>Halogen
  <td><sub>
</tr>
<tr>
  <td>
  <td><sub>Chromaticity Coordinates (CIE 1931/<var>2<sup>o</sup></var>)
  <td><sub>
  <td><sub>x = 0.43</br>
  y = 0.40
  <td><sub>
  <td><sub>
  <td><sub>
  <td><sub>
  <td><sub>
  <td><sub>
</tr>
<tr>
  <td>
  <td><sub>Wavelength (<var>λ<sub>P</sub></var>) [nm]
  <td><sub>375
  <td><sub>410-780
  <td><sub>626
  <td><sub>525
  <td><sub>470
  <td><sub>850
  <td><sub>850
  <td><sub>850
</tr>
<tr>
  <td>
  <td><sub>Spectrum half width (Δλ) [nm]
  <td><sub>9
  <td><sub>
  <td><sub>20
  <td><sub>40
  <td><sub>26
  <td><sub>45
  <td><sub>45
  <td><sub>45
</tr>
<tr>
  <td>
  <td><sub>Luminous intensity <var>I<sub>V</sub></var> [mcd]</br>(by I = 12 mA)
  <td><sub>
  <td><sub>13800
  <td><sub>1920
  <td><sub>2400
  <td><sub>1200
  <td><sub>
  <td colspan=2><sub>
</tr>
<tr>
  <td>
  <td><sub>Luminous flux (<var>Φ<sub>V</sub></var>) [lm]
  <td><sub>
  <td><sub>
  <td><sub>1.0
  <td><sub>1.2
  <td><sub>0.6
  <td><sub>
  <td colspan=2><sub>
</tr>
<tr>
  <td>
  <td><sub>Viewing angle (2θ) [<sup>o</sup>]
  <td><sub>15
  <td><sub>40
  <td colspan=3><sub>25
  <td><sub>18
  <td colspan=2><sub>18
</tr>
<tr>
  <td>
  <td><sub>Ø [mm]
  <td colspan=8><sub>5
</tr>
<tr>
  <td>
  <td><sub>Length [mm]
  <td><sub>8.3
  <td><sub>8.65
  <td colspan=3><sub>8.6
  <td><sub>8.6
  <td colspan=2><sub>8.6
</tr>
<tr>
  <td>
  <td><sub>Long leg
  <td><sub>Anode (+)
  <td><sub>Anode (+)
  <td colspan=3><sub>Common Cathode (-)
  <td><sub>Anode (+)
  <td colspan=2><sub>Anode (+)
</tr>
<tr>
  <td>
  <td><sub><var>I<sub>F</sub></var> [mA]
  <td><sub>20
  <td><sub>25
  <td colspan=3><sub>35
  <td><sub>100
  <td colspan=2><sub>100
</tr>
<tr>
  <td>
  <td><sub><var>V<sub>R</sub></var> [V]
  <td><sub>4
  <td><sub>5
  <td colspan=3><sub>5
  <td><sub>5
  <td colspan=2><sub>5
</tr>
<tr>
  <td>
  <td><sub><var>V<sub>F</sub></var> [V]</br>(by I = 12 mA)
  <td><sub>3.4
  <td><sub>2.9
  <td><sub>1.93
  <td><sub>2.9
  <td><sub>3.4
  <td><sub>1.3
  <td colspan=2><sub>1.3
</tr>
<tr>
  <td>
  <td><sub>Calculated series resistor [Ω]
  <td><sub>0
  <td><sub>33.3
  <td><sub>114.2
  <td><sub>33.3
  <td><sub>0
  <td><sub>175
  <td colspan=2><sub>175
</tr>
<tr>
  <td>
  <td><sub>Series resistor [Ω]
  <td><sub>0
  <td><sub>62
  <td><sub>182
  <td><sub>62
  <td><sub>0
  <td><sub>182
  <td colspan=2><sub>182
</tr>
<tr>
  <td>
  <td><sub>GPIO
  <td><sub>12
  <td><sub>12
  <td><sub>12
  <td><sub>13
  <td><sub>14
  <td><sub>23
  <td><sub>12
  <td><sub>23
</tr>
<tr>
  <td colspan=2><sub><b>Cuvette</b>
  <td><sub><a href='https://www.amazon.de/gp/product/B07NNGHKSC/ref=ppx_yo_dt_b_asin_title_o04_s00?ie=UTF8&psc=1'>UV quartz cuvette</a>
  <td><sub><a href='https://www.amazon.de/gp/product/B07NNGHKSC/ref=ppx_yo_dt_b_asin_title_o04_s00?ie=UTF8&psc=1'>UV quartz cuvette</a>
  <td colspan=4><sub>Normal glass (soda-lime glass)
  <td colspan=2><sub>Normal glass (soda-lime glass)
</tr>
<tr>
  <td>
  <td><sub>Material
  <td><sub>UV transmitting quartz
  <td><sub>UV transmitting quartz
  <td colspan=4><sub>Normal glass (soda-lime glass)
  <td colspan=2><sub>Normal glass (soda-lime glass)
</tr>
<tr>
  <td>
  <td><sub>Chemical and heat resistant
  <td colspan=8><sub>Yes
</tr>
<tr>
  <td>
  <td><sub>Transmission range [nm]
  <td><sub>190-2500
  <td><sub>190-2500
  <td colspan=4><sub>350-2500
  <td colspan=2><sub>350-2500
</tr>
<tr>
  <td>
  <td><sub>Form
  <td><sub>Square
  <td><sub>Square
  <td colspan=4><sub>Round
  <td colspan=2><sub>Round
</tr>
<tr>
  <td>
  <td><sub>Polished sidewalls
  <td><sub>2
  <td><sub>2
  <td colspan=4><sub>N/A
  <td colspan=2><sub>N/A
</tr>
<tr>
  <td>
  <td><sub>L x W x H [mm]
  <td><sub>12.5 x 12.5 x 45.0
  <td><sub>12.5 x 12.5 x 45.0
  <td colspan=4><sub>N/A
  <td colspan=2><sub>N/A
</tr>
<tr>
  <td>
  <td><sub>Ø x H [mm]
  <td><sub>N/A
  <td><sub>N/A
  <td colspan=4><sub>16.0 x 200.0
  <td colspan=2><sub>16.0 x 200.0
</tr>
<tr>
  <td>
  <td><sub>Wall thickness [mm]
  <td><sub>1.25
  <td><sub>1.25
  <td colspan=4><sub>1.00
  <td colspan=2><sub>1.00
</tr>
<tr>
  <td>
  <td><sub>Light path length [mm]
  <td><sub>10.0
  <td><sub>10.0
  <td colspan=4><sub>14.0
  <td colspan=2><sub>14.0
</tr>
<tr>
  <td>
  <td><sub>Sample volume [ml]
  <td><sub>3.5
  <td><sub>3.5
  <td colspan=4><sub>>5
  <td colspan=2><sub>>5
</tr>
<tr>
  <td colspan=2><sub><b>Light sensor</b>
  <td><sub><a href='https://www.vishay.com/docs/84277/veml6070.pdf'>VEML6070</a>
  <td><sub><a href='https://cdn-shop.adafruit.com/datasheets/TCS34725.pdf'>TCS34725</a>
  <td colspan=4><sub><a href='https://cdn-shop.adafruit.com/datasheets/TSL25911_Datasheet_EN_v1.pdf'>TSL2591</a>
  <td colspan=2><sub><a href='https://cdn-shop.adafruit.com/datasheets/TSL25911_Datasheet_EN_v1.pdf'>TSL2591</a>
</tr>
<tr>
  <td>
  <td><sub>Wavelength (<var>λ<sub>P</sub></var>) [nm]
  <td><sub>355
  <td><sub>525
  <td colspan=3><sub>650
  <td><sub>850
  <td colspan=2><sub>850
</tr>
<tr>
  <td>
  <td><sub>Spectrum half width (Δλ) [nm]
  <td><sub>20
  <td><sub>125
  <td colspan=3><sub>150
  <td><sub>42
  <td colspan=2><sub>42
</tr>
<tr>
  <td>
  <td><sub>Spectrum range (<var>λ<sub>R</sub></var>) [nm]
  <td><sub>320-380
  <td><sub>380-780
  <td colspan=3><sub>380-780
  <td><sub>780-910
  <td colspan=2><sub>780-910
</tr>
<tr>
  <td>
  <td><sub>Voltage [V]
  <td colspan=8><sub>3.3-5.0
</tr>
<tr>
  <td>
  <td><sub>I2C GPIO
  <td colspan=8><sub>SCL: 5</br>SDA: 4
</tr>
<tr>
  <td>
  <td><sub>I2C address
  <td><sub>0x10
  <td><sub>0x29
  <td colspan=4><sub>0x29
  <td colspan=2><sub>0x29
</tr>
<tr>
  <td>
  <td><sub>L x W x H [mm]
  <td><sub>13.0 x 12.0 x 2.0
  <td><sub>20.3 x 20.3 x 2.0
  <td colspan=4><sub>19.0 x 16.5 x 2.0
  <td colspan=2><sub>19.0 x 16.5 x 2.0
</tr>
<tr>
  <td colspan=2><sub><b>Microcontroller</b>
  <td colspan=8><sub><a href='https://cdn.shopify.com/s/files/1/1509/1638/files/ESP_-_32_NodeMCU_Developmentboard_Datenblatt_AZ-Delivery_Vertriebs_GmbH_10f68f6c-a9bb-49c6-a825-07979441739f.pdf?v=1598356497'>ESP32-WROOM-32 NodeMCU WLAN/WiFi</a>
</tr>
<tr>
  <td>
  <td><sub>L x W x H [mm]
  <td colspan=8><sub>48.3 x 25.4 x 10.0
</tr>
<tr>
  <td>
  <td><sub>Firmware
  <td colspan=8><sub><a href='/firmware/bin/ESP_Easy_mega_20201102_test_ESP32_4M316k-factory.bin'>ESP_Easy_mega_20201102_test_ESP32_4M316k-factory.bin</a>
</tr>
<tr>
  <td>
  <td><sub>Update
  <td colspan=8><sub><a href='/firmware/bin/ESP_Easy_mega_20201102_test_ESP32_4M316k-factory.bin'>Via Web-GUI by using OTA (Over the Air)</a>
</tr>
<tr>
  <td colspan=2><sub><b>Case</b>
  <td colspan=8><sub>OpenSCAD 3D model (<a href='./setup/case/smartPhotometer-3d-model.scad'>smartPhotometer-3d-model.scad</a>)
</tr>
<tr>
  <td>
  <td><sub>3D printing
  <td colspan=8><sub>via STL exports
</tr>
<tr>
  <td>
  <td><sub>Filament
  <td colspan=8><sub>Black PLA
</tr>
<tr>
  <td>
  <td><sub>Layer height [mm]
  <td colspan=8><sub>0.2
</tr>
<tr>
  <td rowspan=4>
  <td rowspan=4><sub>STL exports
  <td><sub><a href='./setup/case/3d-printing/smart-UV-Photometer-Case.stl'>smart-UV-Photometer-Case.stl</a>
  <td><sub><a href='./setup/case/3d-printing/smart-Colorimeter-Case.stl'>smart-Colorimeter-Case.stl</a>
  <td colspan=4><sub><a href='./setup/case/3d-printing/smart-RGB-Photometer-Case.stl'>smart-RGB-Photometer-Case.stl</a>
  <td colspan=2><sub><a href='./setup/case/3d-printing/smart-IR-Turbidimeter-Case.stl'>smart-IR-Turbidimeter-Case.stl</a>
</tr>
<tr>
  <td colspan=8><sub><a href='./setup/case/3d-printing/smartPhotometer-Case-Lid.stl'>smartPhotometer-Case-Lid.stl</a>
</tr>
<tr>

  <td colspan=8><sub><a href='./setup/case/3d-printing/smartPhotometer-Cover-for-square-Cuvette.stl'>smartPhotometer-Cover-for-square-Cuvette.stl</a>
</tr>
<tr>
  <td><sub><a href='./setup/case/3d-printing/smart-UV-Photometer-Cuvette-Holder.stl'>smart-UV-Photometer-Cuvette-Holder.stl</a>
  <td><sub><a href='./setup/case/3d-printing/smart-Colorimeter-Cuvette-Holder.stl'>smart-Colorimeter-Cuvette-Holder.stl</a>
  <td colspan=4><sub><a href='./setup/case/3d-printing/smart-RGB-Photometer-Cuvette-Holder.stl'>smart-RGB-Photometer-Cuvette-Holder.stl</a>
  <td colspan=2><sub><a href='./setup/case/3d-printing/smart-IR-Turbidimeter-Cuvette-Holder.stl'>smart-IR-Turbidimeter-Cuvette-Holder.stl</a>
</tr>
</table>

## Sources

- [David Harvey (DePauw University) "Analytical Chemistry 2.1", Chemistry LibreTexts (TM) 2020, 10.](https://chem.libretexts.org/Bookshelves/Analytical_Chemistry/Book%3A_Analytical_Chemistry_2.1_(Harvey))
- [Bruce Justin Lindbloom: http://www.brucelindbloom.com/](http://www.brucelindbloom.com/)
- [Chandler Abraham "A Beginner’s Guide to (CIE) Colorimetry", 2016](https://medium.com/hipster-color-science/a-beginners-guide-to-colorimetry-401f1830b65a)

</br>
<br /><span xmlns:dct="http://purl.org/dc/terms/" property="dct:title">smartPhotometer</span> by <a xmlns:cc="http://creativecommons.org/ns#" href="https://github.com/smartaquametering" property="cc:attributionName" rel="cc:attributionURL">smartAquaMetering</a> is licensed under a <a rel="license" href="http://creativecommons.org/licenses/by-sa/4.0/">Creative Commons Attribution-ShareAlike 4.0 International License</a>.<br />Based on a work at <a xmlns:dct="http://purl.org/dc/terms/" href="https://github.com/smartaquametering/smartPhotometer" rel="dct:source">https://github.com/smartaquametering/smartPhotometer</a>.<br />For permissions beyond the scope of this license see <a xmlns:cc="http://creativecommons.org/ns#" href="https://github.com/smartaquametering/smartPhotometer/blob/main/LICENSE" rel="cc:morePermissions">https://github.com/smartaquametering/smartPhotometer/blob/main/LICENSE</a>.

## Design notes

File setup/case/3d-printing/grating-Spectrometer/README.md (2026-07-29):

# DIY Spectroscope with USB Webcam and Grating

Origional Project:

- https://www.thingiverse.com/thing:3351995/comments
- https://cults3d.com/en/3d-model/various/diy-spectroscope-with-usb-webcam-and-grating

Design author: Quas7

- https://www.thingiverse.com/Quas7/designs
- https://cults3d.com/en/users/Quas7

This is an optical spectroscope for near-UV to near-IR spectroscopy based on a CMOS webcam in conjunction with an optical grating (i.e. 1000 lines grating).
It works with free software (for non-commercial use), like the very sophisticated SpectraGryph and the less complex Theremino Spectrometer v2.7 or with Public Lab online via spectralworkbench.org.

- https://www.effemm2.de/spectragryph/
- http://www.theremino.com/en/downloads/automation#spectrometer
- https://publiclab.github.io/spectral-workbench.js/examples/new-capture/

I added two reference measurement figures of my setup with a 1000 lines/mm grating.
First figure shows the calibration based on an energy saving lamp and its Hg-lines (436nm, 546nm calibration lines) and the other figure is a proof measurement of a green laser (532nm). Accuracy is quite good and completely sufficient for my needs.

A fitting webcam for this purpose is the AUSDOM 1080p Full HD PRo Webcam. It is easy to disassemble (only 4 screws) and the IR filter in the objective can be removed (tip: attach a strip of Tesa on the filter first in case it cracks). Of course, any LED of the webcam has to be cut off as well.

The whole assembly consists of 5 parts:
- case base for mounting and adjusting everything
- camera fixture (for AUSDOM 1080p PCB here)
- Grating frame holder
- Slit holder
- case top lid

For the assembly you will also need
- one bare webcam (without housing) like an AUSDOM 1080p Pro
- graiting foil (1000 or 500 lines)
- 2 blades or similar for the slit
- 2x M3 20mm screw + nuts + washers

I attached the camera pcb and the grating foil with superglue to the respective holders.
2x M3 20mm with nuts and washers fix the camera and the grating holder to the base.
The grating holder should be adjusted to the 140° marking and the camera to the 150° marking. Other ratios are possible for increased resolution but might be harder to adjust to.

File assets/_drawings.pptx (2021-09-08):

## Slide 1

Database

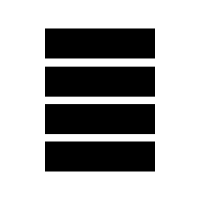
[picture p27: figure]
database Icon 1968097

MQTT-Broker

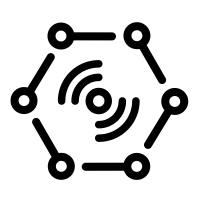
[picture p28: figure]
internet of things Icon 358751
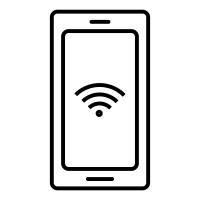
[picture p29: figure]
mobile phone Icon 2008073

Analyst

IoT

smart-RGB-Photometer

http

P2P

ESP32

smart-Thermometer

smart-IR-Turbidimeter

ESP32

P2P

ESP32

P2P

ESP32

smart-pH-Meter

ESP32

P2P

P2P

P2P

ESP32

smart-Colorimeter

P2P

ESP32

smart-EC-Meter

smart-UV-Photometer

ESP32

smart-ORP-Meter

ESPEasy P2P Networking

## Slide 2


Database

mqtt

http

http

Analyst

MQTT-Broker

MQTT
subscribe
publish

ESPEasy
P2P network

IoT

smart-Thermometer

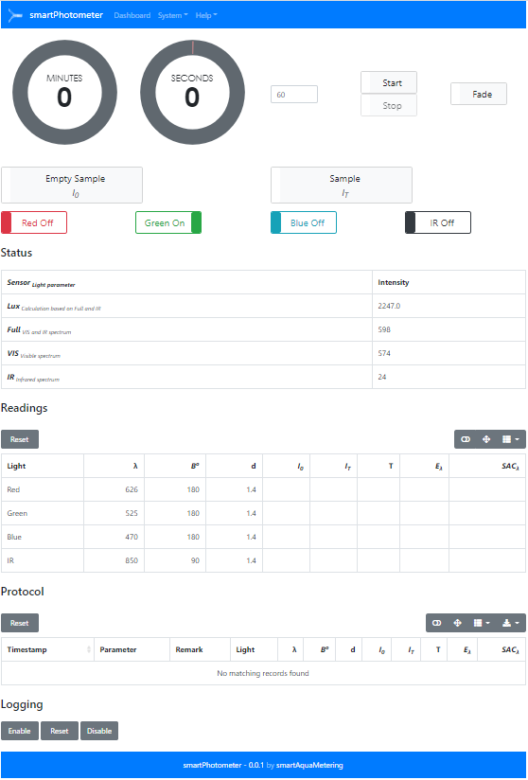
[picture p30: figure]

smart-RGB-Photometer

ESP32

smart-UV-Photometer

ESP32

ESP32

smart-pH-Meter

smart-IR-Turbidimeter

ESP32

ESP32

ESP32

ESP32

ESP32

smart-EC-Meter

smart-Colorimeter

smart-ORP-Meter

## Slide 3

Empty Sample

λ

I0

Beam angle
180 ⁰

Transmitted light measurement

Sample
Colored solution

ελ , c

d

Cuvette

0.66484

Monochromatic light of an defined range of wavelengths

λ

IT

Tλ, Eλ, SACλ, c

Radiation
Source

Absorbance of
complementary
colors

Display and processing
units

Light
sensor

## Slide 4

Empty Sample

λ

I0

Gaussian bandpass filter

X: 0.4980
Y: 0.3774
Z: 0.0759

Beam angle
180 ⁰

Transmitted light measurement

Sample
Colored solution

ελ , c

d

Cuvette

λ

IT

Tλ, Eλ, SACλ, c

Radiation
Source

Absorbance of
complementary
colors

Display and processing
units

Polychromatic light

RGB
sensor

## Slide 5

Empty Sample

λ

I0

Gaussian bandpass filter

410: 0.66484
435: 0.62345
460: 0.39876
485: 0.16654
…

Beam angle
180 ⁰

Transmitted light measurement

Sample
Colored solution

ελ , c

d

Cuvette

λ

IT

Tλ, Eλ, SACλ, c

Radiation
Source

Absorbance of
complementary
colors

18 channel
spectral
sensor

Display and processing
units

Polychromatic light

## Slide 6

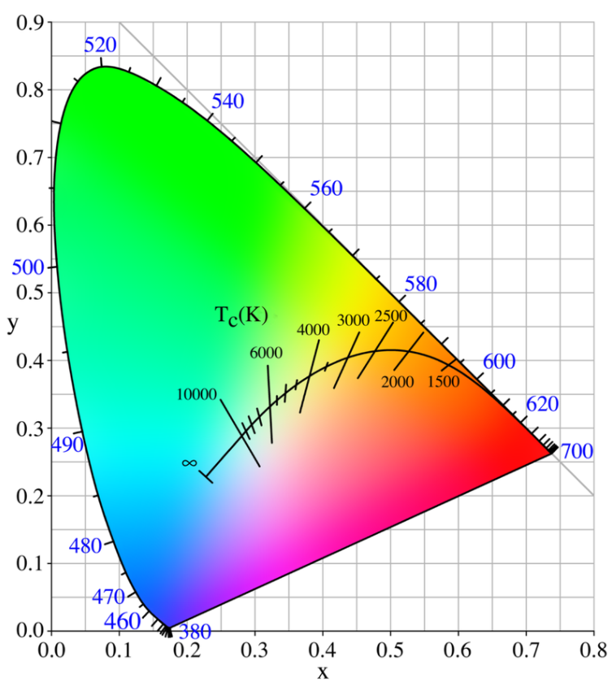
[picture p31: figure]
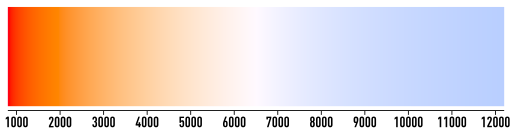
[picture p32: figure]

Color temperature (in K)

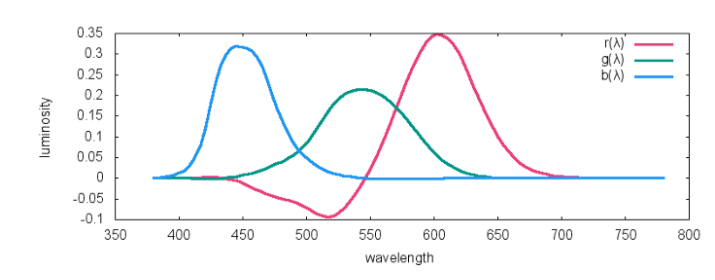
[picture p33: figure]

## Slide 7

Transmission

Absorption

Scattering
Reflexion

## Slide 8

Transmission

Absorption

Scattering
Reflexion

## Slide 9

Reflexion

Transmission

Scattering

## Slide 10

Absorbance
Transmitted light measurement

Beam angle

1.25678

180 ⁰

Nephelometric turbidity
Scattered light measurement

90 ⁰

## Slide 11

E

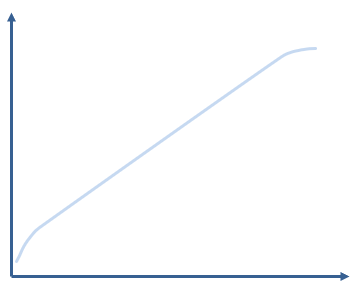
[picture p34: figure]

Δc

ΔEλ

N

c

Measurement range

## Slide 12

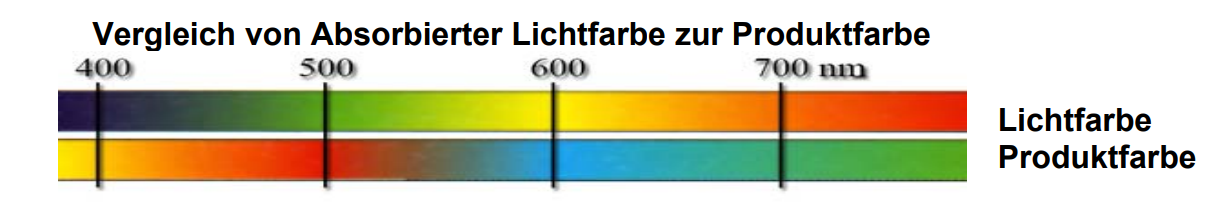
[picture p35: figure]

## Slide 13

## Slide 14

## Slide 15

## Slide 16

375

470

525

626

850

Light sensor

VEML6070

TSL2591

Relative luminous intensity / spectral response

Spectrum half width (Δλ)

9

26

Green

40

20

Red

45

IR

Light source (LED)

UVA

Blue

λ [nm]

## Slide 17

465

525

615

RGB sensor

TCS34725

Relative luminous intensity / spectral response

Spectrum half width (Δλ)

Light source (LED)

λ [nm]

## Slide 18

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
Spectral sensor

AS7265x

Relative luminous intensity / spectral response

Spectrum half width (Δλ)

Light source (LED)

λ [nm]

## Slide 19

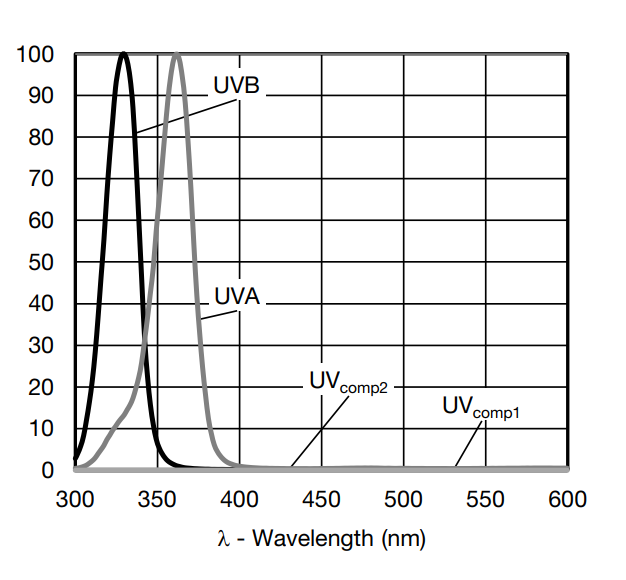
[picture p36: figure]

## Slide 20

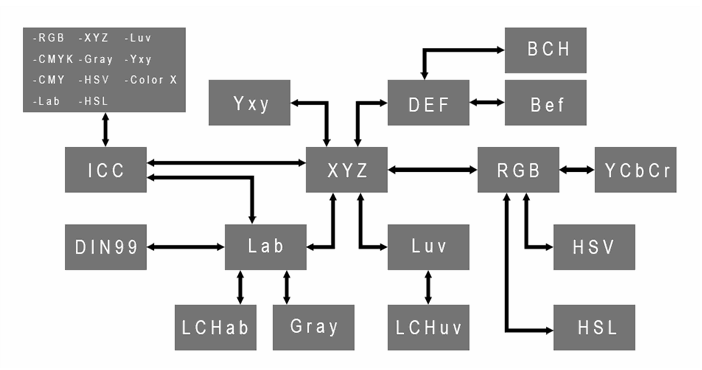
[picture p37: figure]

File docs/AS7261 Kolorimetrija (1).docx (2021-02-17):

PROJEKAT IZ PREDMETA PRIMENJENA OPTOELEKTRONIKA

Tema rada:

Implementacija interfejsa za senzor AS7261 u razvojnom okruženju

„ mikromedia Plus for STM32 “

Student: Tatjana Šestić E1 67/19

Mentor: doc. Jovan Bajić

# SADRŽAJ

# 1. Fotometrijske i analogne radiometrijske veličine

Radiometrija se bavi mjerenjem veličina elektromagnetskih zračenja.

Fotometrija se bavi mjerenjem veličina svjetlosti tako da rezultati odgovaraju osjećaju vida standardnog posmatrača. Vid je vrlo složene i subjektivne prirode jer zavisi od: očiju, očnih nerava i centralnog nervnog sistema. Vid zavisi i od uslova gledanja: prilagođenosti oka, ugla pod kojim se vidi površina i mjesta na mrežnjači na koje se projektuje površina. Da bi se postigao cilj fotometrije, da rezultati mjerenja odgovaraju osjećaju vida, neophodno je korišćenje matematičkih funkcija koje opisuju vid standardnog posmatrača koji je i prosječan posmatrač. Te funkcije daju vezu između fizičkih veličina svjetlosti i ljudskog vida. [1]

U tabeli 1 data je analogija između fotometrijskih i radiometrijskih veličina.

Tabela 1 Analogija između fotometrijskih i radiometrijskih veličina [1]

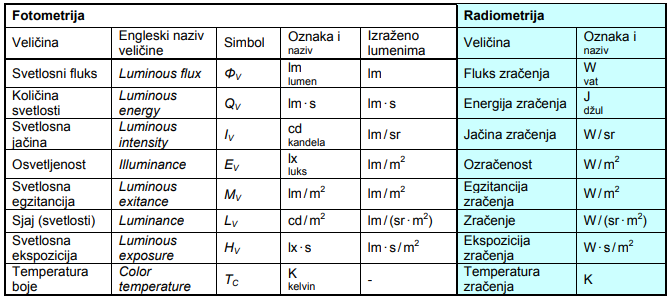
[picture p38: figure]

# 2. Kolorimetrija

Boja je osjećaj koji predstavlja odgovor čovjekovog vizuelnog sistema na pobudu u vidu elektromagnetnog zračenja poznatog kao svjetlost, odnosno predstavlja rezultat dejstva svjetlosti (elektromagnetnog zračenja u vidljivom opsegu - 400 do 700 nm) na mrežnjaču ljudskog oka. Postoje tri vrste fotoreceptora čepića i upravo upravo oni određuju tri promjenjive pomoću kojih se mogu opisati sve boje koje čovjek vidi. S obzirom da su štapići zaduženi za noćni vid, njihov uticaj na percepciju boja može se zanemariti. [2]

Kolorimetrija je nauka koja se bavi numeričkim opisivanjem boja i omogućava podudaranje boja upotrebom različitih mjernih uređaja.

3. Zakoni zračenja apsolutno crnog tijela

- Usljed termalnog kretanja molekula i atoma, svako tijelo na temperaturi iznad apsolutne temperature zrači elektromagnetne talase.
- Sa porastom temperature raste intenzitet termalnog kretanja i količina zračenja koje ono emituje.
- Promjena temperature tela u znatnoj mjeri utiče i na vrstu zračenja.
- Eksperimentalno je utvrđeno da tijelo na temperaturi od oko 500 ⁰C zrači vidljivu crvenkastu svetlost.
- Spektralna raspodela emitovane svjetlosti mijenja se sa promjenom temperature.
- Na istim temeraturama bolje zrače tijela koja bolje apsorbuju toplotno zračenje.
- Glavni faktor koji utiče na ovaj proces je boja tijela.
- Tijela crne boje više zrače od tijela drugih boja.
- Tijela crne boje takođe više i apsorbuju toplotu od tijela drugih boja.
- Takvo tijelo koje predstavlјa idealni apsorber i emiter zračenja zove se - apsolutno crno tijelo. [3]

Plankov zakon zračenja

Pokušaji teorijskog određivanja emisione moći zračenja apsolutnog crnog tijela sa aspekta klasične fizike nisu bili uspješni.

Spektar toplotnog zračenja, odnosno grafik koji pokazuje zavisnost spektralne emisione moći od talasne dužine, dobijen je eksperimentalnim putem. Pokušaji da se dobijeni eksperimentalni rezultati objasne zakonima klasične fizike propali su. Teorijski dobijena kriva na osnovu klasičnih zakona se u oblasti dužih talasnih dužina poklapa sa eksperimentalnom, ali u oblasti kraćih talasnih dužina teži beskonačnosti. Znači, na osnovu objašnjenja klasične fizike, emisiona moć zračenja apsolutno crnog tijela u oblasti kraćih talasnih dužina teži beskonačnosti što nije u skladu sa eksperimentalnim rezultatima i zakonom o održanju energije. Taj paradoks je popularno nazvan “ultraviolentna katastrofa”. [4] (slika 1)

Njemački naučnik Plank 1900. godine, proučavajući problem zračenja apsolutno crnog tijela, postavio je teoriju kvanta.

On je pretpostavio da se zračenje tijela vrši u strogo određenim količinama energije, tzv. kvantima.

Ideja o fotonima (kvantima) znači sljedeće: energija elektromagnetnih talasa ima zrnastu strukturu. Ova zrnca energije su u stvari fotoni (kvanti). Plankova formula za energiju jednog fotona pokazuje da različiti elektromagnetni talasi imaju fotone nejednakih energija. Kako je energija fotona obrnuto srazmjerna talasnoj dužini zračenja, to znači da minimalnu energiju fotona imaju elektromagnetni talasi sa maksimalnom talasnom dužinom – a to su radio talasi, dok maksimalnu energiju fotona ima onaj dio spektra koji ima minimalne talasne dužine – a to su kosmički zraci. [4]

Energija kvanta je funkcija frekvencije ν. Ako se elektromagnetno zračenje emituje u vidu kvanta, pri čemu je energija svakog kvanta hν, onda je ukupna emitovana energija [3]:

E=nhν (n=1,2,3…) – kvantni broj (1)

h = 6,62 x 10^(-34) Js - Plankova konstanta

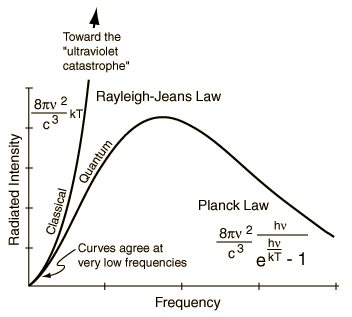
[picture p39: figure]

Slika 1 Plankov zakon zračenja [3]

Plankov zakon zračenja definiše gustinu energije zračenja crnog tijela kao funkciju temperature T i frekvencije ν:

u(ν,T)=(8πhν^3)/(c^3)1/(e^((hν)/(kT)) -1)↔u(λ,T)=(8πhc)/(λ^5)1/(e^((hc)/(λkT)) -1) (2)

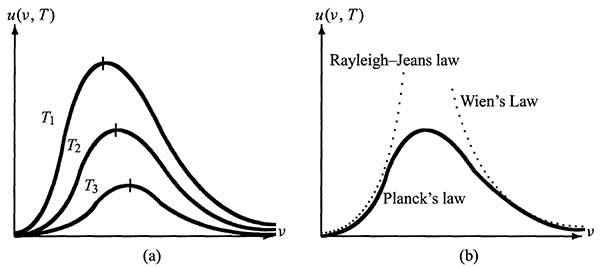
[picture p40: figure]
Maks Plank

Slika 2 Poklapanje teorijskih i eksperimentalnih rezultata zračenja apsolutno crnog tijela [3]

Takođe, na CIE dijagramu boje (slika 4) obično je prikazan Plankov lokus koji predstavlja krivu koja se dobija kada se na dijagramu boja spoje sve tačke koje odgovaraju bojama crnog tijela na različitim temperaturama.

4. CIE XYZ PROSTOR BOJA

RGB i CMY prostori boja pogodni za hardversku implementaciju (npr. monitori i štampači). Međutim, s druge strane, operater (čovjek) nije u stanju da na način koji je jednostavan za interpretaciju zada ili opiše boju u RGB ili CMY prostoru (npr. u RGB prostoru, koliko procenata crvene, zelene i plave boje sadrži određena boja). Boju koju registruje, čovjek opisuje na osnovu njenog tona, zasićenosti i svjetline. Upravo kako bi se elementi trokomponentnog prostora boja približili načinu na koji čovjek opisuje boje, predloženi su prostori boja koji se zasnivaju na tonu boje, zasićenosti i svjetlini boje, odnosno prostori boja orijentisani ka korisnicima. [2]

1920-ih, David Wright i John Guild nezavisno su izveli niz eksperimenata koji su postavili temelje za specifikaciju CIE XYZ prostora boja. Na osnovu rezultata Wright-a i Guild-a CIE komisija je 1931. definisala standardnog posmatrača i usvojila spektralne krive podudaranja boje definisane upravo za standardnog posmatrača. [2] (slika 3)

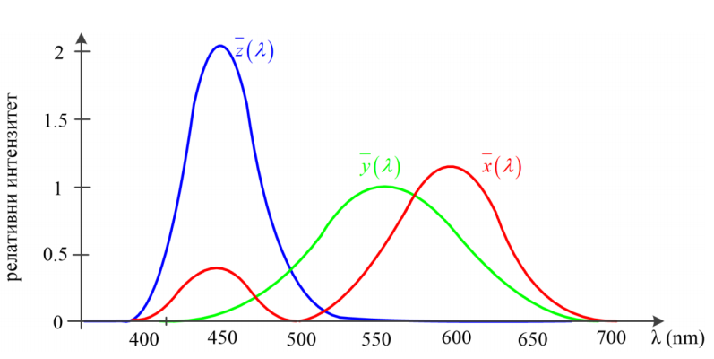
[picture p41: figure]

Slika 3 CIE 1931 xyz krive podudaranja boja [2]

Primjenom ovih krivih spektralna raspodela snage spoljašnje pobude C(λ) (neke boje ili izvora svetlosti, odnosno svjetlosti koja pada na mrežnjaču ljudskog oka) može se transformisati u tri brojčane vrednosti X, Y i Z koje opisuju boju pobude. Prikazano na slici 4.

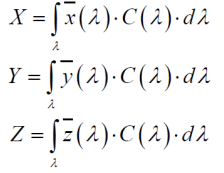
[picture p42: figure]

Slika 4 X, Y, Z vrijednosti formiraju CIE XYZ prostor boja [2]

X, Y i Z se obično nazivaju tristimulusnim vrednostima. CIE XYZ prostor boja je namjerno dizajniran tako da je Y parametar mjera sjajnosti. Normalizacijom X, Y i Z parametara boje dobijaju se vrednosti x, y i z, [2]:

x=X/(X+Y+Z) (3)

y=Y/(X+Y+Z) (4)

z=Z/(X+Y+Z) (5)

Na osnovu prethodnih izraza 3, 4 i 5 može se zaključiti da se z može dobiti i kao z = 1- (x + y), pa je za opis boje dovoljno poznavati x, y i Y.

x i y nazivaju se koordinatama hromatičnosti ili hromatskim koordinatama i opisuju boju u smislu tona boje (crvena, zelena, plava) i zasićenosti (sadžaj bijele boje u datoj boji). Treći parameter Y opisuje sjajnost. [2]

Koordinate hromatičnosti projektuju trodimenzionalni prostor boja CIE XYZ u ravan xy, koja se još naziva i hromatski dijagram. Svaka fizički ostvariva boja (ili sve boje koje čovjek razlikuje) može se predstaviti kao tačka unutar hromatskog dijagrama koji ima jasno definisane granice. [2] (slika 5)

5. Korelisana temperatura boje, CCT (eng. Correlated color temperature)

Temperatura boje (eng. color temperature), T_c , je temperatura (usijanog) crnog tijela koje zrači svjetlost boje iste kao i svjetlost čija se temperatura boje određuje. Temperaturom boje se jednostavno, samo jednim brojem, opisuje boja svjetlosti. [1]

1992. godine McCamy [6,7] je predložio jednostavnu formulu za procjenu Tc pomoću hromatskih koordinata x i y, za CCT u opsegu od 2000 K do 12 500 K [5]:

Tc=an^3 +bn^2 +cn+d (6)

Gdje je: a = −437, b = 3601, c = −6861, d = 5514.31 i :

n=(x-x^e)/(y-y^e) (7)

x^e =0.3320; y^e =1858; [5]

Distribuciona temperatura boje (eng. distribution color temperature), je temperatura boje svjetlosti čiji je spektar sličan spektru crnog tijela u opsegu talasnih dužina od 380 nm do 780 nm.

Za svetlost sijalice sa užarenim vlaknom (inkandescentne sijalice) određuje se distribuciona temperatura boje. Sijalice sa užarenim vlaknom zrače svjetlost čija je distribuciona temperatura boje približno jednaka temperaturi njihovog vlakna. Distribuciona temperatura svjetlosti sijalice zavisi od emisivnosti njene niti i za većinu sijalica je 2 ili 3 K viša od temperature vlakna, ali ima tipova čija je distribuciona temperatura boje i oko 50 K viša od temperature vlakna. [1]

Korelisana temperatura boje je temperatura boje svjetlosti čiji se spektar znatno razlikuje od spektra crnog tijela. Takav znatno različit, linijski spektar svjetlosti, imaju LED lampe. Za vrijednost korelisane temperature boje, daje se temperatura crnog tijela koje zrači svjetlost najsličnije boje sa svjetlošću čija se temperatura boje određuje. Korelisana temperature boje praktično se određuje iz dijagrama boja (slika 5).

Temperature boja iznad 5000 K zovu se hladnim bojama, a niže temperature, između 2700 K i 3000 K, toplim bojama. [1]

U tabeli 2 su date temperature boja nekih svjetlosti. Na slici 5, xy dijagramu boja, označene su svjetlosti crnih tijela različitih temperatura i neke standardne svjetlosti.

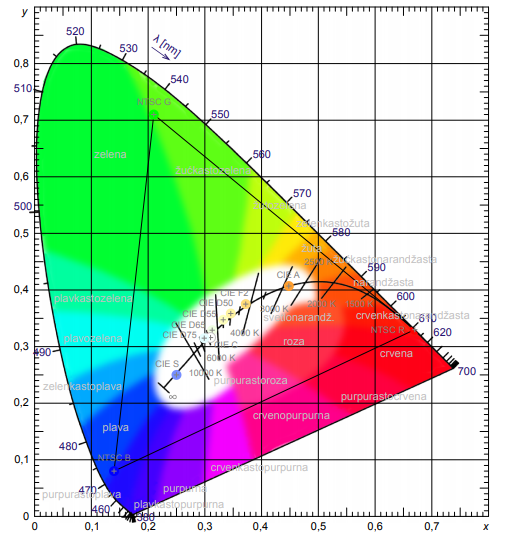
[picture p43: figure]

Slika 5 xy dijagram boja (sistem CIE 1931) [1]

Slika 5 - xy dijagram boja (sistem CIE 1931.) sa označenim: monohromatskim svjetlostima (po obodu „potkovice“), oblastima boja, RGB primarima (NTSC 1953), standardnim svjetlostima (CIE), i krivom boje svetlosti crnih tijela različitih temperatura. (Svaka od boja je najzasićenija koju može da prikaže CRT monitor računara)

Tabela 2 Temperature boja i koordinate svetlosti [1]

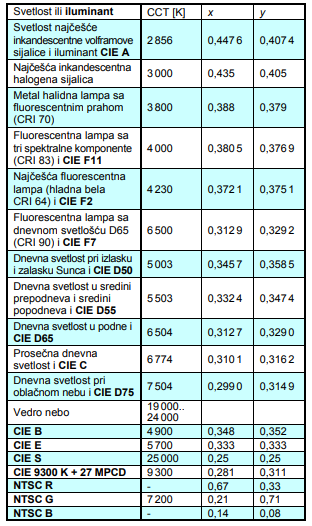
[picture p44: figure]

6. Osvjetljenost, LUX (eng. illuminance)

Osvjetljenost, E_v , za površinu dA osvetljenu fluksom d Φ_v , definisana je jednačinom:

E_v =(dΦ_v)/(dA) (8)

Osvjetljenost (lx) površine, je gustina svjetlosnog fluksa na toj površini (slika 1). Najveća osvjetljenost površine, E_(vMAX) , pri istim ostalim parametrima, se dobija kada se površina postavi normalno na snop svjetlosti. Kada snop zaklapa ugao 0 sa normalom na površinu. [1]

E_v = E_(vMAX) x cos0 (9)

Pri konstantnoj gustini fluksa na površini A, E_v = Φ_v /A .

Osvetljenost E_v , površine normalne na snop svetlosti iz tačkastog izvora na rastojanju r i svjetlosne jačine I_v , je:

E_v =(I_v)/(r^2) (10)

Osvjetljenost površine koju osvjetljava više izvora svjetlosti, jednaka je zbiru osvjetljenosti koje bi dao svaki od izvora samostalno. Neke osvetljenosti navedene su u tabeli 3.

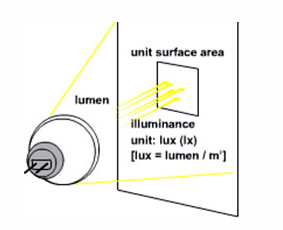
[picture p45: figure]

Slika 6 LUX [8]

Tabela 3 Osvetljenost nekih površina [1]

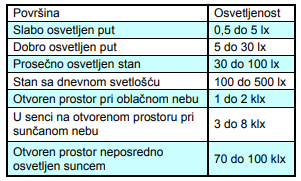
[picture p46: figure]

# 7. Senzor AS7261

Ovaj senzor je hromatski bijeli senzor boje i omogućava direktno određivanje XYZ koordinata konzistentnih sa CIE 1931 prostorom boja, odnosno standardnim posmatračem. Omogućava precizno određivanje korelisane temperature boje (CCT), takođe integriše i NEAR-IR kanal za druge aplikacije. Senzor posjeduje i LED drajvere (LED_IND, LED_DRV) sa programabilnim strujama. Nalazi se u LGA kućištu na kojem se nalazi otvor za kontrolu svetlosti. Kontrola i pristup spektralnim podacima omogućena je upotrebom UART serijske komunikacije, odnosno AT komandi. UART komunikacija vrši se brzinom od 115 200 bps i nije je moguće menjati. Podržava poruke od 8 bit-a, bez Parity bit-a i sa jednim STOP bit-om. [9]

Preciznost senzora dolazi od korišćenja 16-bit AD konvertora integrisanog u senzor. Senzor radi na naponu napajanja od 3.3 V i ima mogućnost povezivanja spoljašnje memorije korišćenjem I2C protokola. Modul koji je korišćen u projektu nema mogućnost pristupa pinovima za dodavanje spoljašnje memorije. Senzor ima validne vrijednosti mjerenja u temperaturnom opsegu od -40 do 85 ˚C. [9]

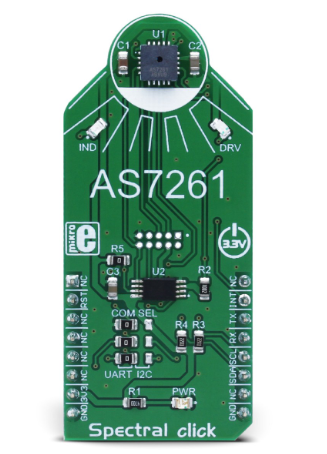
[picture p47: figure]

Slika 7 Senzor AS7261 [10]

# 8. Razvojno okruženje Mikromedia Plus for STM32

Mikromedia Plus je razvojno okruženje u vlasništvu kompanije Mikroelektronika. Srž razvojnog okruženja je moćni STM32F746ZG (https://www.st.com/en/microcontrollers/stm32f746zg.html) ARM Cortex M4 mikrokontroler koji može da radi na maksimalnoj frekvenciji od 216 MHz. Predstavlja moćan alat za izradu GUI aplikacija, s obzirom da posjeduje programabilni displej koji funkcioniše na dodir. Displej veličine 4.3” upravljan je od strane SSD1963 grafičkog kontrolera obezbjeđuje kristalno jasne slike rezolucije 480x272 px. Pored pomenutih razvojno okruženje posjeduje i niz drugih korisnih modula, ali u ovom projektu nisu korišćeni. Detaljnije informacije mogu se naći na adresama u literaturi. [10]

Prikaz razvojnog okruženja dat je na slici 3.

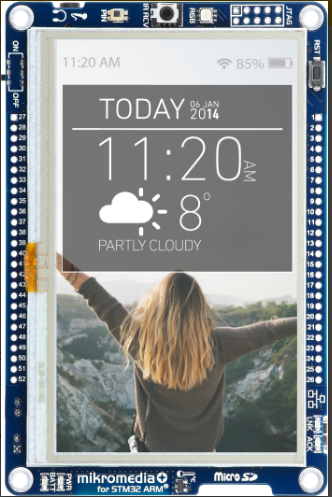
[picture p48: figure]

Slika 8 Mikromedia Plus razvojno okruženje [10]

# 9. Povezivanje senzora i razvojnog sistema

S obzirom da senzor AS7261 prenosi podatke preko serijske komunikacije, i na razvojnom okruženju omogućen je UART i to na pinovima C6 i C7, koji predstavljaju izlazne pinove.

RX senzora treba povezati na RX razvojnog okruženja, odnosno C6, a TX senzora na TX razvojnog okruženja, tj. C7.

Skica povezivanja prikazana je na slici 9.

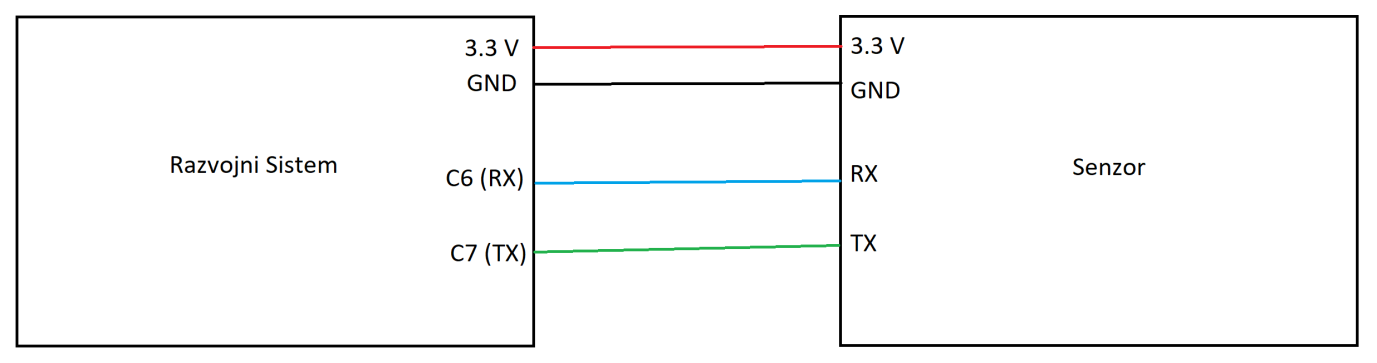
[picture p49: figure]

Slika 9 Skica povezivanja senzora i razvojnog sistema

Provjera uspostavljenosti komunikacije između senzora i razvojnog sistema vrši se pritiskom na taster START nakon pokretanja aplikacije.

# 10. Zadatak projekta

Senzorom je omogućeno mjerenje korelisane temperature boje (CCT) i osvjetljenosti (LUX) i prikazivanje tih vrijednosti a displeju, kao i prikaz trenutne vrijednosti na progres-baru čija početna i krajnja vrijednost pripadaju opsezima koji odgovaraju sijalicama sa užarenim vlaknom i LED sijalicama.

Nakon pokretanja aplikacije i pokretanja displeja, pritiskom na tarter START vršti se provjera komunikacije (slika 10).

Po uspostavljanju komunikacije, pokreće se sljedeći prozor na displeju, na kojem korisnik može podešavati vrijeme integracije i pojačanje senzora. Paralelno se vrši i mjerenje CCT i LUX. (slika 11)

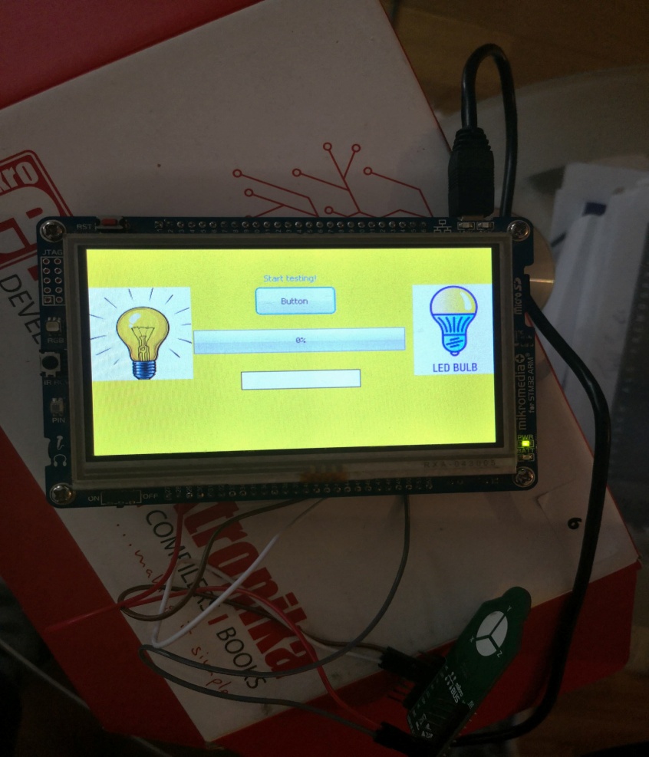
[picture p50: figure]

Slika 10 START Window


Slika 11 Prikaz mjerenja na displeju

# 11. Testiranje

Testiranje je vršeno na tri različite sijalice, CFL (EconomyTwister 8W WW E14 220-240V 1PF/6), GLS (Inkandescentna sijalica E14 P45 - 40W - 220V - 2700K) i fluo cijev (neonka T5 – 840 – 14 W).

Rezultati pri vremenu integracije od 20 ms i pojačanju 1 su prikazani u tabeli 4.

Tabela 4 Rezultati mjerenja CCT

Vrsta sijalice | Izmjerena CCT | Deklarisana CCT
CFL | 2676 K | 2700 K
GLS | 2833 K | 2700 K
Neonka | 3852 K | 4000 K

Testiranje je vršeno na rastojanju od 30 cm od izvora osvjetljenja i senzor nije bio izložen direktnom svjetlu, već je bio postavljen pod uglom.

Tabela 5 Izmjereni LUX

Vrsta sijalice | Izmjereni LUX | Deklarisani svjetlosni fluks
CFL | 89 lux (lm/ m^2 ) | 500 lm
GLS | 121 lux (lm/ m^2 ) | 405 lm
Neonka | 154 lux (lm/ m^2 ) | 1300 lm

# 12. Zaključak

Ovaj senzor omogućava:

- Mjerenje boje i optičke gustine(apsorbancije)
- Podudaranje i identifikaciju boja
- Preciznu kalibraciju/podešavanje boja

Mjerenja su dala rezultate izuzetno bliske deklarisanim vrijednostima za pojedine izvore osvjetljenja, što potvrđuje preciznost i robustnost senzora AS7261.

# 13. Literatura

[1] Kostić, G. (2013), Fotometrija, SYMMETRY, SY295.

[2] https://www.optolab.ftn.uns.ac.rs/, pristupljeno 20.02.2020.

[3] http://nasport.pmf.ni.ac.rs/materijali/487/Predavanja%2009.12.2014..ppt, pristupljeno 20.02.2020.

[4] https://fizis.rs/ Plankova teorija zračenja

[5] Li, C., Cui, G., Melgosa, M., Ruan, X., Zhang, Y., Ma, L., Xiao, K., Luo, M, ''Accurate method for computing correlated color temperature'', Vol. 24, No. 13, OPTICS EXPRESS (2016).

[6] C. S. McCamy, “Correlated color temperature as an explicit function of chromaticity coordinates,” Color Res. Appl. 17(2), 142–144 (1992).

[7] C. S. McCamy, “Correlated color temperature as an explicit function of chromaticity coordinates (Erratum)”, Color Res. Appl. 18(2), 150 (1993).

[8] http://www.ohopt.com/led.asp, pristupljeno 23.02.2020.

[9] https://ams.com/as7261, pristupljeno 20.02.2020.

[10] https://www.mikroe.com/mikromedia-4-stm32f7, pristupljeno 20.02.2020.

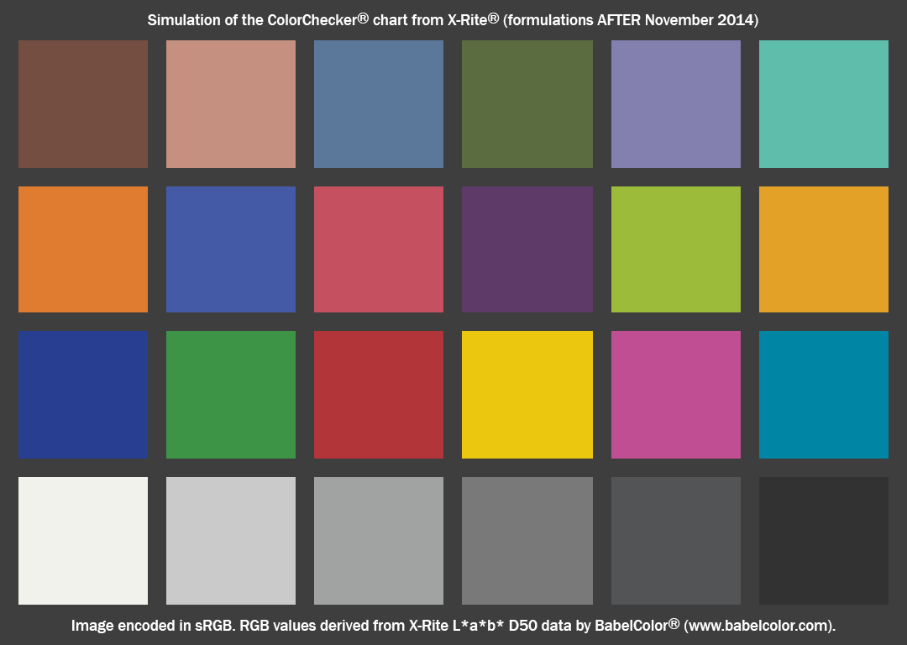
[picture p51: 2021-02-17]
assets/ColorChecker_sRGB_from_Lab_D50_AfterNov2014.tif

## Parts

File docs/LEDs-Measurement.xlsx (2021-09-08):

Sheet: LED-Laser-Lamp
 |  |  |  | LED | RGB LED | Laser
 |  |  |  |  |  |  |  | Δλ |  | Ø
 |  |  |  |  |  |  |  |  |  |  |  |  |  |  |  |  |  |  |  |  |  |  |  |  |  | 3.3 | 12 |  | 6.0 | 12.0
 |  |  |  |  |  |  |  | [nm] | [nm] |  |  |  |  |  | [o] | [lm/W] | [lm] | [mcd] | [mW] | [mW] | [mA] | [V] | [V] | [V] | [V] | [V] | [mA] | [Ω] |  |  |  | [Ω]
Product | Shop | Light color | Material | Peak Emmision Wavelength | Column1 | Column2 | No | Spectrum Half Width | FWHM Bandwidth | Diameter | Column3 | Length | Long Leg | Lens Color | Viewing Angle | Effizienz | Luminous flux | Luminous Intensity | Radiant Flux | Power Dissipation | Forward Current | Forward Voltage Min | Forward Voltage Max | Forward Voltage Typ | Forward Voltage | GPIO | Column4 | Calculated series resistor | Column7 | Column6 | Column5 | Series resistor
Nichia NSPU510CS |  | UV |  | 375 |  |  | 1 | 10 | 370-380 | 5 | 5.3 | 8.3 | Anode (+) | Water Clear | 40 |  |  |  | 15.1 | 80 | 20 | 2.90 | 4.00 | 3.30 | 3.25 | 12 |  | 4.2 | 225.0 |  |  | 4.3 - 5.0 | 4 | 1 | 0
LL-504UVAC2E-Q5C |  | UV |  | 395 |  |  | 2 | 40 | 375-415 | 5 | 5.85 | 8.65 | Anode (+) | Water Clear | 15 |  |  | 350 |  |  |  |  |  |  |  | 13 |  | 275.0 | 500.0 |  |  |  | 5 |  | 1 | TX
Violett-Laserpointer | LaserPointerPro | Violet | - | 405 |  | 405 | L1 | - | - | - | - | - | - | - | - | - | - | - | - | 20 | - | - | - | 5.00 | 5.00 | - | - | -141.7 | 83.3 |  |  | - |  | 2 | 2
TRU-5004PCH02 | Conrad | Violet |  | 405 |  |  |  | - | - | 5 |  |  |  | Water Clear | 15 |  |  | 500 |  |  | 20 |  |  | 3.50 |  |  |  |  | 208.3 |  |  |  |  | 3 | 3 | RX
LUMITRONIX-UV | leds.de | Violet |  | 407 |  |  |  | 15 | 400-415 | 5 | 5.9 | 8.6 | Anode (+) | Water Clear | 15 | 0.00 | 0.03 | 293 |  |  | 20 | 3.13 | 3.31 | 3.20 | 3.08 |  |  | 18.7 | 233.3 |  |  | 19 |  |  | 4 | I2C
LL-504UVC2E-Q5C | Reichelt | Violet | InGaN | 415 |  |  | 3 | 44 | 393-437 | 5 | 5.85 | 8.65 | Anode (+) | Water Clear | 15 |  |  | 350 |  | 95 | 25 | 2.80 | 3.80 | 3.20 | 3.05 | 14 |  | 20.8 | 233.3 |  |  | 21 |  |  | 5 | I2C
EVERLIGHT 383UBC/H2 | Reichelt | Blue | GaN/SiC | 428 |  |  | 4 | 40 | 418-458 | 5 | 5.85 | 8.65 | Anode (+) | Water Clear | 30 |  |  | 630 |  | 70 | 30 |  |  |  |  | 27 |  | 275.0 | 500.0 |  |  |  |  |  | 6 | internal flash
Blue-Laserpointer | ebay | Blue |  | 445 |  | 445 |  |  |  |  |  |  |  |  |  |  |  |  |  |  |  |  |  |  |  |  |  | 275.0 | 500.0
KINGBRIGHT L-7113QBC-D | Reichelt | Blue | InGaN | 460 |  |  | 5 | 50 | 435-485 | 5 | 5.9 | 8.6 | Anode (+) | Water Clear | 20 |  |  | 4500 |  | 120 | 20 |  | 4.00 | 3.30 | 3.10 | 26 |  | 16.7 | 225.0 |  |  | 17 |  |  | 7 | internal flash
Nichia NSPB500AS |  | Blue | InGaN | 470 |  |  | 6 | 40 | 450-490 | 5 | 5.3 | 8.3 | Anode (+) | Water Clear | 15 |  |  | 11000 |  | 123 | 20 | 2.60 | 3.50 | 3.20 | 3.08 | 25 |  | 18.7 | 233.3 |  |  | 19 |  |  | 8 | internal flash
LL-509RGBC2E-006 | Reichelt | Blue | InGaN | 470 | 470 |  | B | 26 | 460-486 | 5 | 5.9 | 8.6 | Anode (+) | Water Clear | 25 |  |  | 700 |  | 90 | 25 | 2.60 | 3.60 | 3.20 | 2.95 |  |  | 29.2 | 233.3 |  |  | 30 |  |  | 9 | internal flash
Nichia NEPE510JS |  | Blue-Green | InGaN | 498 |  |  |  | 24 | 486-510 | 5 | 5.3 | 8.3 | Anode (+) | Water Clear | 30 |  |  | 25500 |  | 120 | 35 | 2.70 | 3.45 | 3.10 | 3.12 |  |  | 14.6 | 241.7 |  |  | 15 |  |  | 10 | internal flash
SLOAN L5BG1N | Reichelt nicht lieferbar | Blue-Green | InGaN | 500 |  |  |  | 35 | 485-520 | 5 | 5.3 | 8.3 | Anode (+) | Water Clear | 10 |  |  | 12000 |  | 120 | 30 | 3.60 | 4.00 |  | 3.60 |  |  | -25.0 | 500.0 |  |  | 0 |  |  | 11 | internal flash
LL-504BGC2E-G3-1BC |  | Blue-Green | InGaN | 500 |  |  | 7 | 30 | 485-515 | 5 | 5.9 | 8.6 | Anode (+) | Water Clear | 15 |  |  | 20000 |  | 95 | 25 | 2.80 | 3.80 | 3.20 | 3.04 | 33 |  | 21.7 | 233.3 |  |  | 22 |  | 4 | 12
LL-504PGC2E-G4-1BC |  | Green | InGaN | 510 |  |  |  | 35 | 492-527 | 5 | 5.9 | 8.6 | Anode (+) | Water Clear | 15 |  |  | 39000 |  | 95 | 25 | 2.80 | 3.80 | 3.20 | 3.04 |  |  | 21.7 | 233.3 |  |  | 22 |  | 5 | 13
KINGBRIGHT L-7113ZGC | Reichelt | Green | InGaN | 515 |  |  | 8 | 30 | 500-530 | 5 | 5.9 | 8.6 | Anode (+) | Water Clear | 20 |  |  | 27000 |  | 102.5 | 25 |  | 4.10 | 3.30 | 3.20 | 32 |  | 8.3 | 225.0 |  |  | 9 |  | 6 | 14
LL-504PGC2E-G5-2CC | Reichelt | Green | InGaN | 525 |  |  | 9 | 35 | 510-545 | 5 | 5.9 | 8.6 | Anode (+) | Water Clear | 15 |  |  | 39000 |  | 95 | 25 | 2.80 | 3.80 | 3.20 | 3.03 | 15 |  | 22.5 | 233.3 |  |  | 23 |  | 7 | 15
LL-509RGBC2E-006 | Reichelt | Green | InGaN | 525 | 525 |  | G | 40 | 505-545 | 5 | 5.9 | 8.6 | Anode (+) | Water Clear | 25 |  |  | 4000 |  | 90 | 25 | 2.60 | 3.60 | 3.20 | 3.03 |  |  | 22.5 | 233.3 |  |  | 23 |  | 8 | 16
Nichia NSPG500DS |  | Green | InGaN | 525 |  |  |  | 35 | 510-545 | 5 | 5.3 | 8.6 | Anode (+) | Water Clear | 15 | 32 | 2 | 37700 |  | 126 | 35 |  | 3.60 | 3.20 | 3.12 |  |  | 14.6 | 233.3 |  |  | 15 |  | 9 | 17
 |  |  |  | 445
Green-Laserpointer | LaserPointerPro | Green | - | 532 |  | 532 | L2 | - | - | - | - | - | - | - | - | - | - | - | - | 10 | - | - | - | - | - | - | - | - | - |  |  | - |  | 10 | 18
KINGBRIGHT L-53SGC | Conrad | Green-Yellow | AlGaInP | 565 |  |  | 10 | 30 | 550-580 | 5 | 5.9 | 8.6 | Anode (+) | Water Clear | 30 |  |  | 200 |  | 105 | 25 |  | 2.50 | 2.20 | 2.13 | 2 |  | 97.5 | 316.7 |  |  | 98 |  | 11 | 19
RND 135-00134 | Reichelt | Green-Yellow | AlGaInP | 565 |  |  |  | 40 | 545-585 | 5 | 5.9 | 8.6 | Anode (+) | Green Diffused | 60 |  |  | 30 |  | 78 | 30 | 1.60 | 2.60 | 2.20 | 1.98 |  |  | 110.0 | 316.7 |  |  | 110 |  |  | 20 | no GPIO
KINGBRIGHT L-7113CGCK | Reichelt | Green-Yellow | AlGaInP | 574 |  |  | 11 | 20 | 564-584 | 5 | 5.9 | 8.6 | Anode (+) | Water Clear | 20 |  |  | 1400 |  | 75 | 30 |  | 2.50 | 2.10 | 2.03 | 0 |  | 105.8 | 325.0 |  |  | 106 |  | 12 | 21
LL-583UYC2C-Y2-4DA | Reichelt | Yellow | AlInGaP | 592 |  |  | 12 | 18 | 483-603 | 5 | 5.9 | 8.6 | Anode (+) | Water Clear | 15 |  |  | 14000 |  | 65 | 25 | 1.60 | 2.60 | 2.00 | 1.80 | 16 |  | 125.0 | 333.3 |  |  | 125 |  | 13 | 22
LUMITRONIX-Yellow | leds.de | Yellow | AlGaInP | 593 |  |  |  | 17 | 583-600 | 5 | 5.9 | 8.6 | Anode (+) | Water Clear | 80 | 34.75 | 4.53 | 2347 |  |  | 60 | 2.14 | 2.39 | 2.22 | 1.90 |  |  | 116.7 | 315.0 |  |  | 117 |  | 14 | 23
Nichia NSPA510BS |  | Orange |  | 600 |  |  |  | 115 | 555-670 | 5 | 5.3 | 8.3 | Anode (+) | Water Clear | 30 | 27 | 2 | 7800 |  | 103 | 30 |  | 3.45 | 3.10 | 2.90 |  |  | 33.3 | 241.7 |  |  | 34 |  |  | 24 | no GPIO
EVERLIGHT 383-2UYOC/S400-A7 | Reichelt | Orange |  | 611 |  |  | 13 | 34 | 594-628 | 5 | 5.3 | 8.3 | Anode (+) | Water Clear | 15 |  |  | 11000 |  | 60 | 25 | 1.60 | 2.40 | 2.00 | 1.85 | 17 |  | 120.8 | 333.3 |  |  | 121 |  | 15 | 25
LL-509RGBC2E-006 | Reichelt | Red | AlGaInP | 626 | 626 |  | R | 20 | 606-646 | 5 | 5.9 | 8.6 | Anode (+) | Water Clear | 25 |  |  | 1000 |  | 60 | 25 | 1.60 | 2.40 | 2.00 | 1.82 |  |  | 123.3 | 333.3 |  |  | 124 |  | 16 | 26
Nichia NSPR510GS |  | Red |  | 633 |  |  |  | 15 | 625-640 | 5 | 5.3 | 8.3 | Anode (+) | Water Clear | 30 | 35 | 1 | 9600 |  | 117 | 50 |  | 2.38 | 2.10 | 2.10 |  |  | 100.0 | 325.0 |  |  | 100 |  | 17 | 27
Red-Laserpointer | ebay | Red | - | 635 |  | 635 | L3 | - | - | - | - | - | - | - | - | - | - | - | - | 10 | - | - | - | - | - | - | - | - | - |  |  | - |  |  | 29 | no GPIO
KINGBRIGHT L-7113SEC-J3 | Reichelt | Red | AlGaInP | 640 |  |  | 14 | 25 | 627-652 | 5 | 5.3 | 8.3 | Anode (+) | Water Clear | 20 |  |  | 11000 |  | 84 | 30 |  | 2.80 | 2.20 | 2.13 | 18 |  | 97.5 | 316.7 |  |  | 98 |  |  | 28 | no GPIO
Red-Laserpointer | LaserPointerPro | Red | - | 650 |  | 650 | L3 | - | - | - | - | - | - | - | - | - | - | - | - | 10 | - | - | - | - | - | - | - | - | - |  |  | - |  |  | 29 | no GPIO
EVERLIGHT 383-2SDRC/S530-A3 | Reichelt | Red | AlGaInP | 650 |  |  |  | 30 | 635-665 | 5 | 5.9 | 8.6 | Anode (+) | Water Clear | 6 |  |  | 2500 |  | 60 | 25 |  | 2.40 | 2.00 | 1.85 |  |  | 120.8 | 333.3 |  |  | 121 |  |  | 30 | no GPIO
KINGBRIGHT L-7113SRC-DU | Reichelt | Red | AlGaInP | 660 |  |  | 15 | 20 | 650-670 | 5 | 5.9 | 8.6 | Anode (+) | Water Clear | 20 |  |  | 15000 |  | 75 | 30 |  | 2.50 | 2.10 | 1.98 | 19 |  | 110.0 | 325.0 |  |  | 110 |  |  | 31 | no GPIO
KINGBRIGHT L-7113HD | Reichelt | Deep Red |  | 700 |  |  | 16 | 46 | 677-723 |  |  |  |  |  |  |  |  | 5 |  |  |  |  |  |  |  | 21 |  | 275.0 | 500.0 |  |  |  |  | 18 | 32
 |  |  |  | 780 |  |  |  |  |  |  |  |  |  |  |  |  |  |  |  |  |  |  |  |  |  |  |  |  | 500.0 |  |  |  |  | 19 | 33
LL-503KIRC2V-4CD |  | IR | AIGaAs | 830 |  |  | 17 | 55 | 808-863 | 5 | 5.85 | 8.65 | Anode (+) | Water Clear | 30 |  |  |  | 15 | 160 | 20 | 1.20 | 1.60 | 1.40 | 1.50 | 3 |  | 150.0 | 383.3 |  |  | 150 |  |  | 34 | no output
LL-503SIRC2E-5AC |  | IR | AIGaAs | 850 |  |  | 18 | 55 | 828-883 | 5 | 5.85 | 8.65 | Anode (+) | Water Clear | 15 |  |  |  | 15 | 160 | 20 | 1.00 | 1.60 | 1.40 | 1.40 | 22 |  | 158.3 | 383.3 |  |  | 159 |  |  | 35 | no output
 |  |  |  | 850 |  |  |  |  |  |  |  |  |  |  |  |  |  |  |  |  |  |  |  |  |  |  |  | 275.0 | 500.0 |  |  |  |  |  | 36 | no output
OSRAM SFH 4550 |  | IR | AIGaAs | 860 |  |  |  | 55 | 835-890 | 5 | 5.85 | 8.65 | Anode (+) | Water Clear | 3 |  |  |  | 70 | 180 | 20 |  | 1.70 | 1.50 | 1.35 |  |  | 162.5 | 375.0 |  |  | 163 |  |  | 37 | no GPIO | no output
 |  |  |  | 870 |  |  |  |  |  |  |  |  |  |  |  |  |  |  |  |  |  |  |  |  |  |  |  | 275.0 | 500.0 |  |  |  |  |  | 38 | no GPIO | no output
LL-503HIRC2E-5CC |  | IR | AIGaAs | 880 |  |  | 19 | 55 | 858-913 | 5 | 5.85 | 8.65 | Anode (+) | Water Clear | 15 |  |  |  | 12 | 160 | 20 | 1.00 | 1.60 | 1.30 | 1.15 | 23 |  | 179.2 | 391.7 |  |  | 180 |  |  | 39 | no output
 |  |  |  | 880 |  |  |  |  |  |  |  |  |  |  |  |  |  |  |  |  |  |  |  |  |  |  |  | 275.0 | 500.0
LL-503IRC2E-5AC |  | IR | AIGaAs | 940 |  |  | 20 | 55 | 918-973 | 5 | 5.85 | 8.65 | Anode (+) | Water Clear | 15 |  |  |  | 12 | 150 | 20 | 0.80 | 1.50 | 1.20 | 1.20 |  |  | 175.0 | 400.0 |  |  | 175
 |  |  |  | 940 |  |  |  |  |  |  |  |  |  |  |  |  |  |  |  |  |  |  |  |  |  |  |  | 275.0 | 500.0
OSRAM SFH 4544 OSO |  | IR | AIGaAs | 950 |  |  |  | 42 | 923-965 | 5 | 5.85 | 8.65 | Anode (+) | Black | 10 |  |  |  | 550 | 200 | 20 |  | 1.90 | 1.60 | 1.30 |  |  | 166.7 | 366.7 |  |  | 167
IR-Laserpointer | ebay | IR |  | 980 |  | 980 |  | 42 | 923-965 | 5 | 5.85 | 8.65 | Anode (+) | Black | 10 |  |  |  | 550 | 200 | 20 |  | 1.90 | 1.60 | 1.30 |  |  | 166.7 | 366.7 |  |  | 167
Nichia NSDL570GS-K1, 2700K |  |  |  |  |  |  |  |  |  |  |  |  |  |  |  |  |  |  |  |  |  | 1.00
Nichia NSDL510GS-K1, 2800K |  |  |  |  |  |  |  |  |  |  |  |  |  |  |  |  |  |  |  |  |  | 2.00
Nichia NSPL500DS, 3000K |  |  |  |  |  |  |  |  |  |  |  |  |  |  |  |  |  |  |  |  |  | 3.00
Nichia NSPL510DS, 4000K |  |  |  |  |  |  |  |  |  |  |  |  |  |  |  |  |  |  |  |  |  | 4.00
Nichia NSPW500GS-K1, 5000K |  |  |  |  |  |  |  |  |  |  |  |  |  |  |  |  |  |  |  |  |  | 5.00
Nichia NSPW570DS, 6500K |  |  |  |  |  |  |  |  |  |  |  |  |  |  |  |  |  |  |  |  |  | 6.00
OSRAM Halogen EEK: C (A++ - E) G4 33 mm 6 V 10 W Warmweiß 1 St.
OSRAM Halogen G4 31.0 mm 6 V 20 W Kaltweiß Stiftsockel 1 St.
Halogenlampe ECO STAR G4, 7 W, 95 lm, 2700 K, dimmbar
http://zeiss-campus.magnet.fsu.edu/articles/lightsources/leds.html

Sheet: Measurement
Illumination |  | Measurement |  |  |  | Reference |  | Datasheet |  |  |  |  |  |  | Calibration |  | Measured |  | Dominant | CCT | Color |  |  |  | Delta | Delta
Name | Type | PWM | Exposure | Intensity | Averaging | ID | nm | Ref. | Peak | Typ. | Min | Max | FWHM | CCT | Pixel | nm | nm | FWHM | nm | K | x | y | Y | HEX | Reference | Typ.
370nm-Nichia-NSPU510CS (http://www.nichia.co.jp/specification/products/led/NSPU510CS-E.pdf) | Monochromatic-LED | 1907 | -3 | 96.716 | 250 |  | 370.000 | 375 |  |  | 370 | 380 |  |  | 390.03 | 370.00 | 368.78 | 22.50 |  |  |  |  |  |  | 1.22 | 1.22
395nm-Lumitronix-UV (https://www.leds.de/low-budget-5mm-led-uv-300mcd-436nm-15401.html) | Monochromatic-LED | 107 | -3 | 95.9 | 250 |  |  | 407.1 |  |  |  |  |  |  |  |  | 395.03 | 29.01 |  |  |  |  |  |  |  | 12.07
OSRAM-DULUXSTAR-14W | Incandescent-Lamp | n/a | -4 | 56.71 | 250 | Hg | 404.656 | 404.656 |  |  |  |  |  |  | 445.83 | 404.66 | 403.22 | 19.00 |  |  |  |  |  |  | 1.44 | 1.44
425nm-EverLight-383UBC-H2 | Monochromatic-LED | 4095 | -3 | 96.422 | 250 |  |  | 428 |  |  |  |  |  |  |  |  | 422.90 | 99.51 |  |  |  |  |  |  |  | 5.10
OSRAM-DULUXSTAR-14W | Incandescent-Lamp | n/a | -4 | 80.054 | 250 | Hg | 435.833 | 435.833 |  |  |  |  |  |  | 498.01 | 435.83 | 436.09 | 25.50 |  |  |  |  |  |  | 0.26 | 0.26
470nm-Kingbright-L-7113QBC-D | Monochromatic-LED | 172 | -3 | 93.958 | 250 |  |  | 465 |  |  |  |  |  |  |  |  | 471.03 | 40.72 |  |  |  |  |  |  |  | 6.03
500nm-Nichia-NEPE510JS | Monochromatic-LED | 161 | -3 | 99.604 | 250 |  |  | 498.1 |  |  |  |  |  |  |  |  | 498.12 | 40.65 |  |  |  |  |  |  |  | 0.02
520nm-Kingbright-L-7113ZGC | Monochromatic-LED | 215 | -3 | 99.869 | 250 |  |  | 515 |  |  | 525 |  |  |  |  |  | 518.27 | 45.80 | 522.7 | 8292.8 | 0.146937 | 0.711973 | 0.295647 | #00bb10 |  | 3.27
530nm-Nichia-NSPG500DS (https://docs.rs-online.com/9576/0900766b80e762bf.pdf) | Monochromatic-LED | 100 | -3 | 94.424 | 250 |  |  | 525 |  |  |  |  |  |  |  |  | 532.32 | 52.98 |  |  |  |  |  |  |  | 7.32
OSRAM-DULUXSTAR-14W | Incandescent-Lamp | n/a | -4 | 104 | 250 | Hg | 546.074 | 546.074 |  |  |  |  |  |  | 667.88 | 546.07 | 546.28 | 33.97 |  |  |  |  |  |  | 0.21 | 0.21
575nm-Kingbright-L-7113CGCK | Monochromatic-LED | 679 | -3 | 98.721 | 250 |  |  | 574 |  |  | 570 |  |  |  |  |  | 572.69 | 40.70 |  |  |  |  |  |  |  | 1.31
595nm-Lumitronix-Yellow | Monochromatic-LED | 140 | -3 | 95.733 | 250 |  |  | 593.3 |  |  | 589.8 | 590.8 |  |  |  |  | 594.23 | 33.35 | 589.8 | 1730.2 | 0.574019 | 0.425302 | 0.229227 | #ca6900 |  | 0.93
610nm-EverLight-383-2UYOC-S4 | Monochromatic-LED | 32 | -3 | 94.711 | 250 |  |  | 611 |  |  | 605 |  |  |  |  |  | 612.18 | 36.36 |  |  |  |  |  |  |  | 1.18
OSRAM-DULUXSTAR-14W | Incandescent-Lamp | n/a | -4 | 143 | 250 | Hg | 614.948 | 614.948 |  |  |  |  |  |  | 774.46 | 614.95 | 616.30 | 56.53 |  |  |  |  |  |  | 1.35 | 1.35
635nm-Kingbright-L-7113SEC-J3 | Monochromatic-LED | 54 | -3 | 101.83 | 250 |  |  | 625 | 640 | 625 |  |  | 25 |  |  |  | 632.65 | 40.34 |  |  |  |  |  |  |  | 7.65
660nm-Kingbright-L-7113SRC-DU | Monochromatic-LED | 129 | -3 | 100.04 | 250 |  |  | 660 |  |  | 640 |  |  |  |  |  | 656.87 | 43.39 |  |  |  |  |  |  |  | 3.13
695nm-Kingbright-L-7113HD | Monochromatic-LED | 4095 | -3 | 92.354 | 250 |  |  | 700 |  |  | 660 |  |  |  |  |  | 693.65 | 82.98 |  |  |  |  |  |  |  | 6.35
850nm-EverLight-HIR-383C-L289 | Monochromatic-LED | 334 | -3 | 98.647 | 250 |  | 850.000 | 850 |  |  |  |  |  |  | 1140.3 | 850.00 | 847.42 | 44.72 |  |  |  |  |  |  | 2.58 | 2.58
950nm-OSRAM-SFH-4544-OSO | Monochromatic-LED | 4095 | -3 | 74.526 | 250 |  | 950.000 | 950 |  |  |  |  |  |  | 1303.1 | 950.00 | 951.27 | 33.78 |  |  |  |  |  |  | 1.27 | 1.27
2700K-Nichia-NSDL570GS-K1 | Broadband LED | 4095 | -3 | 95.447 | 250 |  |  |  |  |  |  |  |  | 2700
2800K-Nichia-NSDL510GS-K1 | Broadband LED | 1648 | -2 | 96.609 | 250 |  |  |  |  |  |  |  |  | 2800
3000K-Nichia-NSPL500DS | Broadband LED | 1120 | -3 | 97.779 | 250 |  |  |  |  |  |  |  |  | 3000
4000K-Nichia-NSPL510DS | Broadband LED | 1605 | -3 | 99.423 | 250 |  |  |  |  |  |  |  |  | 4000
5000K-Nichia-NSPW500GS-K1 | Broadband LED | 1002 | -3 | 96.763 | 250 |  |  |  |  |  |  |  |  | 5000
6500K-Nichia-NSPW570DS | Broadband LED | 1702 | -3 | 98.394 | 250 |  |  |  |  |  |  |  |  | 6500
OSRAM Halogen EEK: C (A++ - E) G4 33 mm 6 V 10 W Warmweiß 1 St. | Incandescent-Lamp
OSRAM Halogen G4 31.0 mm 6 V 20 W Kaltweiß Stiftsockel 1 St. | Incandescent-Lamp
Halogenlampe ECO STAR G4, 7 W, 95 lm, 2700 K, dimmbar | Incandescent-Lamp
Philips | Incandescent-Lamp
 |  |  |  |  |  |  |  |  |  |  |  |  |  |  |  |  |  |  |  |  |  |  |  |  | 1.19 | 3.30

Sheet: Calibration
a) | y = 0.63831033x + 119.96857454
 | R² = 0.99995607
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

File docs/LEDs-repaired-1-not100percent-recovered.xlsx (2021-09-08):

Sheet: LEDs
 |  |  |  | LED | RGB LED | Laser
 |  |  |  |  |  |  |  | Δλ |  | Ø
 |  |  |  |  |  |  |  |  |  |  |  |  |  |  |  |  |  |  |  |  |  |  |  |  |  | 3.3 | 12 |  | 6.0 | 12.0
 |  |  |  |  |  |  |  | [nm] | [nm] |  |  |  |  |  | [o] | [lm/W] | [lm] | [mcd] | [mW] | [mW] | [mA] | [V] | [V] | [V] | [V] | [V] | [mA] | [Ω] |  |  |  | [Ω]
Product | Shop | Light color | Material | Peak Emmision Wavelength | Column1 | Column2 | No | Spectrum Half Width | FWHM Bandwidth | Diameter | Column3 | Length | Long Leg | Lens Color | Viewing Angle | Effizienz | Luminous flux | Luminous Intensity | Radiant Flux | Power Dissipation | Forward Current | Forward Voltage Min | Forward Voltage Max | Forward Voltage Typ. | Forward Voltage | GPIO | Column4 | Calculated series resistor | Column7 | Column6 | Column5 | Series resistor
Nichia NSPU510CS |  | UV |  | 375 |  |  | 1 | 10 | 370-380 | 5 | 5.3 | 8.3 | Anode (+) | Water Clear | 40 |  |  |  | 15.1 | 80 | 20 | 2.90 | 4.00 | 3.30 | 3.25 | 12 |  | 4.2 | 225.0 |  |  | 4.3 - 5.0 | 4 | 1 | 0
LL-504UVAC2E-Q5C |  | UV |  | 395 |  |  | 2 | 40 | 375-415 | 5 | 5.85 | 8.65 | Anode (+) | Water Clear | 15 |  |  | 350 |  |  |  |  |  |  |  | 13 |  | 275.0 | 500.0 |  |  |  | 5 |  | 1 | TX
Violett-Laserpointer | LaserPointerPro | Violet | - | 405 |  | 405 | L1 | - | - | - | - | - | - | - | - | - | - | - | - | 20 | - | - | - | 5.00 | 5.00 | - | - | -141.7 | 83.3 |  |  | - |  | 2 | 2
TRU-5004PCH02 | Conrad | Violet |  | 405 |  |  |  | - | - | 5 |  |  |  | Water Clear | 15 |  |  | 500 |  |  | 20 |  |  | 3.50 |  |  |  |  | 208.3 |  |  |  |  | 3 | 3 | RX
LUMITRONIX-UV | leds.de | Violet |  | 407 |  |  |  | 15 | 400-415 | 5 | 5.9 | 8.6 | Anode (+) | Water Clear | 15 | 0.00 | 0.03 | 293 |  |  | 20 | 3.13 | 3.31 | 3.20 | 3.08 |  |  | 18.7 | 233.3 |  |  | 19 |  |  | 4 | I2C
LL-504UVC2E-Q5C | Reichelt | Violet | InGaN | 415 |  |  | 3 | 44 | 393-437 | 5 | 5.85 | 8.65 | Anode (+) | Water Clear | 15 |  |  | 350 |  | 95 | 25 | 2.80 | 3.80 | 3.20 | 3.05 | 14 |  | 20.8 | 233.3 |  |  | 21 |  |  | 5 | I2C
EVERLIGHT 383UBC/H2 | Reichelt | Blue | GaN/SiC | 428 |  |  | 4 | 40 | 418-458 | 5 | 5.85 | 8.65 | Anode (+) | Water Clear | 30 |  |  | 630 |  | 70 | 30 |  |  |  |  | 27 |  | 275.0 | 500.0 |  |  |  |  |  | 6 | internal flash
Blue-Laserpointer | ebay | Blue |  | 445 |  | 445 |  |  |  |  |  |  |  |  |  |  |  |  |  |  |  |  |  |  |  |  |  | 275.0 | 500.0
KINGBRIGHT L-7113QBC-D | Reichelt | Blue | InGaN | 460 |  |  | 5 | 50 | 435-485 | 5 | 5.9 | 8.6 | Anode (+) | Water Clear | 20 |  |  | 4500 |  | 120 | 20 |  | 4.00 | 3.30 | 3.10 | 26 |  | 16.7 | 225.0 |  |  | 17 |  |  | 7 | internal flash
Nichia NSPB500AS |  | Blue | InGaN | 470 |  |  | 6 | 40 | 450-490 | 5 | 5.3 | 8.3 | Anode (+) | Water Clear | 15 |  |  | 11000 |  | 123 | 20 | 2.60 | 3.50 | 3.20 | 3.08 | 25 |  | 18.7 | 233.3 |  |  | 19 |  |  | 8 | internal flash
LL-509RGBC2E-006 | Reichelt | Blue | InGaN | 470 | 470 |  | B | 26 | 460-486 | 5 | 5.9 | 8.6 | Anode (+) | Water Clear | 25 |  |  | 700 |  | 90 | 25 | 2.60 | 3.60 | 3.20 | 2.95 |  |  | 29.2 | 233.3 |  |  | 30 |  |  | 9 | internal flash
Nichia NEPE510JS |  | Blue-Green | InGaN | 498 |  |  |  | 24 | 486-510 | 5 | 5.3 | 8.3 | Anode (+) | Water Clear | 30 |  |  | 25500 |  | 120 | 35 | 2.70 | 3.45 | 3.10 | 3.12 |  |  | 14.6 | 241.7 |  |  | 15 |  |  | 10 | internal flash
SLOAN L5BG1N | Reichelt nicht lieferbar | Blue-Green | InGaN | 500 |  |  |  | 35 | 485-520 | 5 | 5.3 | 8.3 | Anode (+) | Water Clear | 10 |  |  | 12000 |  | 120 | 30 | 3.60 | 4.00 |  | 3.60 |  |  | -25.0 | 500.0 |  |  | 0 |  |  | 11 | internal flash
LL-504BGC2E-G3-1BC |  | Blue-Green | InGaN | 500 |  |  | 7 | 30 | 485-515 | 5 | 5.9 | 8.6 | Anode (+) | Water Clear | 15 |  |  | 20000 |  | 95 | 25 | 2.80 | 3.80 | 3.20 | 3.04 | 33 |  | 21.7 | 233.3 |  |  | 22 |  | 4 | 12
LL-504PGC2E-G4-1BC |  | Green | InGaN | 510 |  |  |  | 35 | 492-527 | 5 | 5.9 | 8.6 | Anode (+) | Water Clear | 15 |  |  | 39000 |  | 95 | 25 | 2.80 | 3.80 | 3.20 | 3.04 |  |  | 21.7 | 233.3 |  |  | 22 |  | 5 | 13
KINGBRIGHT L-7113ZGC | Reichelt | Green | InGaN | 515 |  |  | 8 | 30 | 500-530 | 5 | 5.9 | 8.6 | Anode (+) | Water Clear | 20 |  |  | 27000 |  | 102.5 | 25 |  | 4.10 | 3.30 | 3.20 | 32 |  | 8.3 | 225.0 |  |  | 9 |  | 6 | 14
LL-504PGC2E-G5-2CC | Reichelt | Green | InGaN | 525 |  |  | 9 | 35 | 510-545 | 5 | 5.9 | 8.6 | Anode (+) | Water Clear | 15 |  |  | 39000 |  | 95 | 25 | 2.80 | 3.80 | 3.20 | 3.03 | 15 |  | 22.5 | 233.3 |  |  | 23 |  | 7 | 15
LL-509RGBC2E-006 | Reichelt | Green | InGaN | 525 | 525 |  | G | 40 | 505-545 | 5 | 5.9 | 8.6 | Anode (+) | Water Clear | 25 |  |  | 4000 |  | 90 | 25 | 2.60 | 3.60 | 3.20 | 3.03 |  |  | 22.5 | 233.3 |  |  | 23 |  | 8 | 16
Nichia NSPG500DS |  | Green | InGaN | 525 |  |  |  | 35 | 510-545 | 5 | 5.3 | 8.6 | Anode (+) | Water Clear | 15 | 32 | 2 | 37700 |  | 126 | 35 |  | 3.60 | 3.20 | 3.12 |  |  | 14.6 | 233.3 |  |  | 15 |  | 9 | 17
 |  |  |  | 445
Green-Laserpointer | LaserPointerPro | Green | - | 532 |  | 532 | L2 | - | - | - | - | - | - | - | - | - | - | - | - | 10 | - | - | - | - | - | - | - | - | - |  |  | - |  | 10 | 18
KINGBRIGHT L-53SGC | Conrad | Green-Yellow | AlGaInP | 565 |  |  | 10 | 30 | 550-580 | 5 | 5.9 | 8.6 | Anode (+) | Water Clear | 30 |  |  | 200 |  | 105 | 25 |  | 2.50 | 2.20 | 2.13 | 2 |  | 97.5 | 316.7 |  |  | 98 |  | 11 | 19
RND 135-00134 | Reichelt | Green-Yellow | AlGaInP | 565 |  |  |  | 40 | 545-585 | 5 | 5.9 | 8.6 | Anode (+) | Green Diffused | 60 |  |  | 30 |  | 78 | 30 | 1.60 | 2.60 | 2.20 | 1.98 |  |  | 110.0 | 316.7 |  |  | 110 |  |  | 20 | no GPIO
KINGBRIGHT L-7113CGCK | Reichelt | Green-Yellow | AlGaInP | 574 |  |  | 11 | 20 | 564-584 | 5 | 5.9 | 8.6 | Anode (+) | Water Clear | 20 |  |  | 1400 |  | 75 | 30 |  | 2.50 | 2.10 | 2.03 | 0 |  | 105.8 | 325.0 |  |  | 106 |  | 12 | 21
LL-583UYC2C-Y2-4DA | Reichelt | Yellow | AlInGaP | 592 |  |  | 12 | 18 | 483-603 | 5 | 5.9 | 8.6 | Anode (+) | Water Clear | 15 |  |  | 14000 |  | 65 | 25 | 1.60 | 2.60 | 2.00 | 1.80 | 16 |  | 125.0 | 333.3 |  |  | 125 |  | 13 | 22
LUMITRONIX-Yellow | leds.de | Yellow | AlGaInP | 593 |  |  |  | 17 | 583-600 | 5 | 5.9 | 8.6 | Anode (+) | Water Clear | 80 | 34.75 | 4.53 | 2347 |  |  | 60 | 2.14 | 2.39 | 2.22 | 1.90 |  |  | 116.7 | 315.0 |  |  | 117 |  | 14 | 23
Nichia NSPA510BS |  | Orange |  | 600 |  |  |  | 115 | 555-670 | 5 | 5.3 | 8.3 | Anode (+) | Water Clear | 30 | 27 | 2 | 7800 |  | 103 | 30 |  | 3.45 | 3.10 | 2.90 |  |  | 33.3 | 241.7 |  |  | 34 |  |  | 24 | no GPIO
EVERLIGHT 383-2UYOC/S400-A7 | Reichelt | Orange |  | 611 |  |  | 13 | 34 | 594-628 | 5 | 5.3 | 8.3 | Anode (+) | Water Clear | 15 |  |  | 11000 |  | 60 | 25 | 1.60 | 2.40 | 2.00 | 1.85 | 17 |  | 120.8 | 333.3 |  |  | 121 |  | 15 | 25
LL-509RGBC2E-006 | Reichelt | Red | AlGaInP | 626 | 626 |  | R | 20 | 606-646 | 5 | 5.9 | 8.6 | Anode (+) | Water Clear | 25 |  |  | 1000 |  | 60 | 25 | 1.60 | 2.40 | 2.00 | 1.82 |  |  | 123.3 | 333.3 |  |  | 124 |  | 16 | 26
Nichia NSPR510GS |  | Red |  | 633 |  |  |  | 15 | 625-640 | 5 | 5.3 | 8.3 | Anode (+) | Water Clear | 30 | 35 | 1 | 9600 |  | 117 | 50 |  | 2.38 | 2.10 | 2.10 |  |  | 100.0 | 325.0 |  |  | 100 |  | 17 | 27
Red-Laserpointer | ebay | Red | - | 635 |  | 635 | L3 | - | - | - | - | - | - | - | - | - | - | - | - | 10 | - | - | - | - | - | - | - | - | - |  |  | - |  |  | 29 | no GPIO
KINGBRIGHT L-7113SEC-J3 | Reichelt | Red | AlGaInP | 640 |  |  | 14 | 25 | 627-652 | 5 | 5.3 | 8.3 | Anode (+) | Water Clear | 20 |  |  | 11000 |  | 84 | 30 |  | 2.80 | 2.20 | 2.13 | 18 |  | 97.5 | 316.7 |  |  | 98 |  |  | 28 | no GPIO
Red-Laserpointer | LaserPointerPro | Red | - | 650 |  | 650 | L3 | - | - | - | - | - | - | - | - | - | - | - | - | 10 | - | - | - | - | - | - | - | - | - |  |  | - |  |  | 29 | no GPIO
EVERLIGHT 383-2SDRC/S530-A3 | Reichelt | Red | AlGaInP | 650 |  |  |  | 30 | 635-665 | 5 | 5.9 | 8.6 | Anode (+) | Water Clear | 6 |  |  | 2500 |  | 60 | 25 |  | 2.40 | 2.00 | 1.85 |  |  | 120.8 | 333.3 |  |  | 121 |  |  | 30 | no GPIO
KINGBRIGHT L-7113SRC-DU | Reichelt | Red | AlGaInP | 660 |  |  | 15 | 20 | 650-670 | 5 | 5.9 | 8.6 | Anode (+) | Water Clear | 20 |  |  | 15000 |  | 75 | 30 |  | 2.50 | 2.10 | 1.98 | 19 |  | 110.0 | 325.0 |  |  | 110 |  |  | 31 | no GPIO
KINGBRIGHT L-7113HD | Reichelt | Deep Red |  | 700 |  |  | 16 | 46 | 677-723 |  |  |  |  |  |  |  |  | 5 |  |  |  |  |  |  |  | 21 |  | 275.0 | 500.0 |  |  |  |  | 18 | 32
 |  |  |  | 780 |  |  |  |  |  |  |  |  |  |  |  |  |  |  |  |  |  |  |  |  |  |  |  |  | 500.0 |  |  |  |  | 19 | 33
LL-503KIRC2V-4CD |  | IR | AIGaAs | 830 |  |  | 17 | 55 | 808-863 | 5 | 5.85 | 8.65 | Anode (+) | Water Clear | 30 |  |  |  | 15 | 160 | 20 | 1.20 | 1.60 | 1.40 | 1.50 | 3 |  | 150.0 | 383.3 |  |  | 150 |  |  | 34 | no output
LL-503SIRC2E-5AC |  | IR | AIGaAs | 850 |  |  | 18 | 55 | 828-883 | 5 | 5.85 | 8.65 | Anode (+) | Water Clear | 15 |  |  |  | 15 | 160 | 20 | 1.00 | 1.60 | 1.40 | 1.40 | 22 |  | 158.3 | 383.3 |  |  | 159 |  |  | 35 | no output
 |  |  |  | 850 |  |  |  |  |  |  |  |  |  |  |  |  |  |  |  |  |  |  |  |  |  |  |  | 275.0 | 500.0 |  |  |  |  |  | 36 | no output
OSRAM SFH 4550 |  | IR | AIGaAs | 860 |  |  |  | 55 | 835-890 | 5 | 5.85 | 8.65 | Anode (+) | Water Clear | 3 |  |  |  | 70 | 180 | 20 |  | 1.70 | 1.50 | 1.35 |  |  | 162.5 | 375.0 |  |  | 163 |  |  | 37 | no GPIO | no output
 |  |  |  | 870 |  |  |  |  |  |  |  |  |  |  |  |  |  |  |  |  |  |  |  |  |  |  |  | 275.0 | 500.0 |  |  |  |  |  | 38 | no GPIO | no output
LL-503HIRC2E-5CC |  | IR | AIGaAs | 880 |  |  | 19 | 55 | 858-913 | 5 | 5.85 | 8.65 | Anode (+) | Water Clear | 15 |  |  |  | 12 | 160 | 20 | 1.00 | 1.60 | 1.30 | 1.15 | 23 |  | 179.2 | 391.7 |  |  | 180 |  |  | 39 | no output
 |  |  |  | 880 |  |  |  |  |  |  |  |  |  |  |  |  |  |  |  |  |  |  |  |  |  |  |  | 275.0 | 500.0
LL-503IRC2E-5AC |  | IR | AIGaAs | 940 |  |  | 20 | 55 | 918-973 | 5 | 5.85 | 8.65 | Anode (+) | Water Clear | 15 |  |  |  | 12 | 150 | 20 | 0.80 | 1.50 | 1.20 | 1.20 |  |  | 175.0 | 400.0 |  |  | 175
 |  |  |  | 940 |  |  |  |  |  |  |  |  |  |  |  |  |  |  |  |  |  |  |  |  |  |  |  | 275.0 | 500.0
OSRAM SFH 4544 OSO |  | IR | AIGaAs | 950 |  |  |  | 42 | 923-965 | 5 | 5.85 | 8.65 | Anode (+) | Black | 10 |  |  |  | 550 | 200 | 20 |  | 1.90 | 1.60 | 1.30 |  |  | 166.7 | 366.7 |  |  | 167
IR-Laserpointer | ebay | IR |  | 980 |  | 980 |  | 42 | 923-965 | 5 | 5.85 | 8.65 | Anode (+) | Black | 10 |  |  |  | 550 | 200 | 20 |  | 1.90 | 1.60 | 1.30 |  |  | 166.7 | 366.7 |  |  | 167
Nichia NSDL570GS-K1, 2700K |  |  |  |  |  |  |  |  |  |  |  |  |  |  |  |  |  |  |  |  |  | 1.00
Nichia NSDL510GS-K1, 2800K |  |  |  |  |  |  |  |  |  |  |  |  |  |  |  |  |  |  |  |  |  | 2.00
Nichia NSPL500DS, 3000K |  |  |  |  |  |  |  |  |  |  |  |  |  |  |  |  |  |  |  |  |  | 3.00
Nichia NSPL510DS, 4000K |  |  |  |  |  |  |  |  |  |  |  |  |  |  |  |  |  |  |  |  |  | 4.00
Nichia NSPW500GS-K1, 5000K |  |  |  |  |  |  |  |  |  |  |  |  |  |  |  |  |  |  |  |  |  | 5.00
Nichia NSPW570DS, 6500K |  |  |  |  |  |  |  |  |  |  |  |  |  |  |  |  |  |  |  |  |  | 6.00
OSRAM Halogen EEK: C (A++ - E) G4 33 mm 6 V 10 W Warmweiß 1 St.
OSRAM Halogen G4 31.0 mm 6 V 20 W Kaltweiß Stiftsockel 1 St.
Halogenlampe ECO STAR G4, 7 W, 95 lm, 2700 K, dimmbar
http://zeiss-campus.magnet.fsu.edu/articles/lightsources/leds.html

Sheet: Sheet3
102 | 2.400000 | 102 | 1 | 200 | 1.89999925 | 1.952462998 | 200 | 0 |  | 0 | 200 | : | 0.000000 | , | 380 | 0 | 0 | 380 | : | 0 | ,
103 | 2.600000 | 103 | 2 | 300 | 1.89999925 |  | 300 | 0 |  | 0 | 300 | : | 0.000000 | , | 381 | 0.003 | 0.3 | 381 | : | 0.3 | ,
104 | 2.700000 | 104 | 3 | 305 | 1.9 |  | 305 | 0 |  | 0 | 305 | : | 0.000000 | , | 382 | 0.002 | 0.2 | 382 | : | 0.2 | ,
105 | 2.800000 | 105 | 4 | 310 | 2.10479091 |  | 310 | 0 |  | 0 | 310 | : | 0.000000 | , | 383 | 0 | 0 | 383 | : | 0 | ,
106 | 2.800000 | 106 | 5 | 315 | 2.19045021 |  | 315 | 0 |  | 0 | 315 | : | 0.000000 | , | 384 | 0.003 | 0.3 | 384 | : | 0.3 | ,
107 | 2.800000 | 107 | 6 | 320 | 1.9 |  | 320 | 0 |  | 0 | 320 | : | 0.000000 | , | 385 | 0 | 0 | 385 | : | 0 | ,
108 | 2.700000 | 108 | 7 | 325 | 2.01316261 |  | 325 | 0 |  | 0 | 325 | : | 0.000000 | , | 386 | 0.002 | 0.2 | 386 | : | 0.2 | ,
109 | 2.800000 | 109 | 8 | 330 | 1.90519999 |  | 330 | 0 |  | 0 | 330 | : | 0.000000 | , | 387 | 0.003 | 0.3 | 387 | : | 0.3 | ,
110 | 2.700000 | 110 | 9 | 335 | 1.89392353 |  | 335 | 0 |  | 0 | 335 | : | 0.000000 | , | 388 | 0.002 | 0.2 | 388 | : | 0.2 | ,
111 | 2.700000 | 111 | 10 | 340 | 1.94468145 |  | 340 | 0 |  | 0 | 340 | : | 0.000000 | , | 389 | 0.002 | 0.2 | 389 | : | 0.2 | ,
112 | 2.600000 | 112 | 11 | 345 | 2.00165455 |  | 345 | 0 |  | 0 | 345 | : | 0.000000 | , | 390 | 0.003 | 0.3 | 390 | : | 0.3 | ,
113 | 2.600000 | 113 | 12 | 350 | 1.79131766 |  | 350 | 0 |  | 0 | 350 | : | 0.000000 | , | 391 | 0.002 | 0.2 | 391 | : | 0.2 | ,
114 | 2.600000 | 114 | 13 | 355 | 2.03763804 |  | 355 | 0 |  | 0 | 355 | : | 0.000000 | , | 392 | 0.003 | 0.3 | 392 | : | 0.3 | ,
115 | 2.700000 | 115 | 14 | 360 | 1.99498955 |  | 360 | 0 |  | 0 | 360 | : | 0.000000 | , | 393 | 0.002 | 0.2 | 393 | : | 0.2 | ,
116 | 2.700000 | 116 | 15 | 365 | 1.98533498 |  | 365 | 0 |  | 0 | 365 | : | 0.000000 | , | 394 | 0.002 | 0.2 | 394 | : | 0.2 | ,
117 | 2.700000 | 117 | 16 | 370 | 2.00868493 |  | 370 | 0 |  | 0 | 370 | : | 0.000000 | , | 395 | 0.003 | 0.3 | 395 | : | 0.3 | ,
118 | 2.600000 | 118 | 17 | 375 | 1.80280512 |  | 375 | 0 |  | 0 | 375 | : | 0.000000 | , | 396 | 0.001 | 0.1 | 396 | : | 0.1 | ,
119 | 2.600000 | 119 | 18 | 380 | 1.89478281 |  | 380 | 0 |  | 0 | 380 | : | 0.000000 | , | 397 | 0.002 | 0.2 | 397 | : | 0.2 | ,
120 | 2.600000 | 120 | 19 | 385 | 1.94544435 |  | 385 | 0 |  | 0 | 385 | : | 0.000000 | , | 398 | 0.003 | 0.3 | 398 | : | 0.3 | ,
121 | 2.500000 | 121 | 20 | 390 | 1.79914803 |  | 390 | 0 |  | 0 | 390 | : | 0.000000 | , | 399 | 0.001 | 0.1 | 399 | : | 0.1 | ,
122 | 2.600000 | 122 | 21 | 395 | 1.90243802 |  | 395 | 0 |  | 0 | 395 | : | 0.000000 | , | 400 | 0.003 | 0.3 | 400 | : | 0.3 | ,
123 | 2.600000 | 123 | 22 | 400 | 2.09000034 |  | 400 | 0.1375373417 |  | 0.1410196388 | 400 | : | 0.141020 | , | 401 | 0.003 | 0.3 | 401 | : | 0.3 | ,
124 | 2.800000 | 124 | 23 | 405 | 2.00020338 |  | 405 | 0.04774038174 |  | 0.0489491167 | 405 | : | 0.048949 | , | 402 | 0.003 | 0.3 | 402 | : | 0.3 | ,
125 | 2.700000 | 125 |  | 410 | 2.10099767 |  | 410 | 0.1485346717 |  | 0.1522954094 | 410 | : | 0.152295 | , | 403 | 0.004 | 0.4 | 403 | : | 0.4 | ,
126 | 2.700000 | 126 |  | 415 | 2.45278664 |  | 415 | 0.5003236417 |  | 0.5129912966 | 415 | : | 0.512991 | , | 404 | 0.003 | 0.3 | 404 | : | 0.3 | ,
127 | 2.600000 | 127 |  | 420 | 2.86343055 |  | 420 | 0.9109675517 |  | 0.9340322673 | 420 | : | 0.934032 | , | 405 | 0.003 | 0.3 | 405 | : | 0.3 | ,
128 | 2.600000 | 128 |  | 425 | 3.93976576 |  | 425 | 1.987302762 |  | 2.037619124 | 425 | : | 2.037619 | , | 406 | 0.004 | 0.4 | 406 | : | 0.4 | ,
129 | 2.500000 | 129 |  | 430 | 6.6050581 |  | 430 | 4.652595102 |  | 4.77039379 | 430 | : | 4.770394 | , | 407 | 0.004 | 0.4 | 407 | : | 0.4 | ,
130 | 2.600000 | 130 |  | 435 | 11.33405206 |  | 435 | 9.381589062 |  | 9.619120775 | 435 | : | 9.619121 | , | 408 | 0.005 | 0.5 | 408 | : | 0.5 | ,
131 | 2.700000 | 131 |  | 440 | 16.9882289 |  | 440 | 15.0357659 |  | 15.41645527 | 440 | : | 15.416455 | , | 409 | 0.004 | 0.4 | 409 | : | 0.4 | ,
132 | 2.700000 | 132 |  | 445 | 24.86369537 |  | 445 | 22.91123237 |  | 23.49132006 | 445 | : | 23.491320 | , | 410 | 0.005 | 0.5 | 410 | : | 0.5 | ,
133 | 2.600000 | 133 |  | 450 | 35.94874101 |  | 450 | 33.99627801 |  | 34.85702709 | 450 | : | 34.857027 | , | 411 | 0.007 | 0.7 | 411 | : | 0.7 | ,
134 | 2.500000 | 134 |  | 455 | 47.01413795 |  | 455 | 45.06167495 |  | 46.20258794 | 455 | : | 46.202588 | , | 412 | 0.005 | 0.5 | 412 | : | 0.5 | ,
135 | 2.400000 | 135 |  | 460 | 59.65654167 |  | 460 | 57.70407867 |  | 59.16508369 | 460 | : | 59.165084 | , | 413 | 0.007 | 0.7 | 413 | : | 0.7 | ,
136 | 2.400000 | 136 |  | 465 | 73.03185667 |  | 465 | 71.07939367 |  | 72.87904723 | 465 | : | 72.879047 | , | 414 | 0.007 | 0.7 | 414 | : | 0.7 | ,
137 | 2.300000 | 137 |  | 470 | 83.84317513 |  | 470 | 81.89071213 |  | 83.96409661 | 470 | : | 83.964097 | , | 415 | 0.008 | 0.8 | 415 | : | 0.8 | ,
138 | 2.300000 | 138 |  | 475 | 92.08147346 |  | 475 | 90.12901046 |  | 92.41097977 | 475 | : | 92.410980 | , | 416 | 0.01 | 1 | 416 | : | 1 | ,
139 | 2.300000 | 139 |  | 480 | 95.9436343 |  | 480 | 93.9911713 |  | 96.37092635 | 480 | : | 96.370926 | , | 417 | 0.011 | 1.1 | 417 | : | 1.1 | ,
140 | 2.200000 | 140 |  | 485 | 95.8432454 |  | 485 | 93.8907824 |  | 96.26799571 | 485 | : | 96.267996 | , | 418 | 0.01 | 1 | 418 | : | 1 | ,
141 | 2.200000 | 141 |  | 490 | 91.64506842 |  | 490 | 89.69260542 |  | 91.96352542 | 490 | : | 91.963525 | , | 419 | 0.013 | 1.3 | 419 | : | 1.3 | ,
142 | 2.200000 | 142 |  | 495 | 85.02932191 |  | 495 | 83.07685891 |  | 85.18027535 | 495 | : | 85.180275 | , | 420 | 0.013 | 1.3 | 420 | : | 1.3 | ,
143 | 2.200000 | 143 |  | 500 | 79.8653675 |  | 500 | 77.9129045 |  | 79.88557518 | 500 | : | 79.885575 | , | 421 | 0.016 | 1.6 | 421 | : | 1.6 | ,
144 | 2.200000 | 144 |  | 505 | 77.05167749 |  | 505 | 75.09921449 |  | 77.00064558 | 505 | : | 77.000646 | , | 422 | 0.017 | 1.7 | 422 | : | 1.7 | ,
145 | 2.300000 | 145 |  | 510 | 75.99992173 |  | 510 | 74.04745873 |  | 75.9222605 | 510 | : | 75.922260 | , | 423 | 0.02 | 2 | 423 | : | 2 | ,
146 | 2.300000 | 146 |  | 515 | 77.23242727 |  | 515 | 75.27996427 |  | 77.18597175 | 515 | : | 77.185972 | , | 424 | 0.023 | 2.3 | 424 | : | 2.3 | ,
147 | 2.400000 | 147 |  | 520 | 80.45383602 |  | 520 | 78.50137302 |  | 80.48894309 | 520 | : | 80.488943 | , | 425 | 0.027 | 2.7 | 425 | : | 2.7 | ,
148 | 2.300000 | 148 |  | 525 | 83.73548286 |  | 525 | 81.78301986 |  | 83.85367769 | 525 | : | 83.853678 | , | 426 | 0.03 | 3 | 426 | : | 3 | ,
149 | 2.100000 | 149 |  | 530 | 86.51648589 |  | 530 | 84.56402289 |  | 86.70509272 | 530 | : | 86.705093 | , | 427 | 0.034 | 3.4 | 427 | : | 3.4 | ,
150 | 2.200000 | 150 |  | 535 | 89.06100911 |  | 535 | 87.10854611 |  | 89.31404052 | 535 | : | 89.314041 | , | 428 | 0.04 | 4 | 428 | : | 4 | ,
151 | 2.100000 | 151 |  | 540 | 90.18744643 |  | 540 | 88.23498343 |  | 90.46899802 | 540 | : | 90.468998 | , | 429 | 0.045 | 4.5 | 429 | : | 4.5 | ,
152 | 2.100000 | 152 |  | 545 | 90.59282531 |  | 545 | 88.64036231 |  | 90.88464065 | 545 | : | 90.884641 | , | 430 | 0.053 | 5.3 | 430 | : | 5.3 | ,
153 | 2.200000 | 153 |  | 550 | 90.43343269 |  | 550 | 88.48096969 |  | 90.72121238 | 550 | : | 90.721212 | , | 431 | 0.06 | 6 | 431 | : | 6 | ,
154 | 2.300000 | 154 |  | 555 | 89.8 |  | 555 | 87.847537 |  | 90.07174186 | 555 | : | 90.071742 | , | 432 | 0.068 | 6.8 | 432 | : | 6.8 | ,
155 | 2.200000 | 155 |  | 560 | 89.17000251 |  | 560 | 87.21753951 |  | 89.42579351 | 560 | : | 89.425794 | , | 433 | 0.077 | 7.7 | 433 | : | 7.7 | ,
156 | 2.200000 | 156 |  | 565 | 88.15595706 |  | 565 | 86.20349406 |  | 88.38607353 | 565 | : | 88.386074 | , | 434 | 0.089 | 8.9 | 434 | : | 8.9 | ,
157 | 2.200000 | 157 |  | 570 | 88.9 |  | 570 | 86.947537 |  | 89.14895483 | 570 | : | 89.148955 | , | 435 | 0.1 | 10 | 435 | : | 10 | ,
158 | 2.200000 | 158 |  | 575 | 92.08291011 |  | 575 | 90.13044711 |  | 92.41245279 | 575 | : | 92.412453 | , | 436 | 0.118 | 11.8 | 436 | : | 11.8 | ,
159 | 2.200000 | 159 |  | 580 | 95.98952607 |  | 580 | 94.03706307 |  | 96.41798005 | 580 | : | 96.417980 | , | 437 | 0.127 | 12.7 | 437 | : | 12.7 | ,
160 | 2.400000 | 160 |  | 585 | 98.9 |  | 585 | 96.947537 |  | 99.40214404 | 585 | : | 99.402144 | , | 438 | 0.147 | 14.7 | 438 | : | 14.7 | ,
161 | 2.400000 | 161 |  | 590 | 99.48309268 |  | 590 | 97.53062968 | 1.025318921 | 100 | 590 | : | 100.000000 | , | 439 | 0.165 | 16.5 | 439 | : | 16.5 | ,
162 | 2.400000 | 162 |  | 595 | 96.81482095 |  | 595 | 94.86235795 |  | 97.26417051 | 595 | : | 97.264171 | , | 440 | 0.182 | 18.2 | 440 | : | 18.2 | ,
163 | 2.300000 | 163 |  | 600 | 92.6 |  | 600 | 90.647537 |  | 92.94263484 | 600 | : | 92.942635 | , | 441 | 0.204 | 20.4 | 441 | : | 20.4 | ,
164 | 2.200000 | 164 |  | 605 | 85.95542185 |  | 605 | 84.00295885 |  | 86.12982314 | 605 | : | 86.129823 | , | 442 | 0.223 | 22.3 | 442 | : | 22.3 | ,
165 | 2.200000 | 165 |  | 610 | 78.99850917 |  | 610 | 77.04604617 |  | 78.99676894 | 610 | : | 78.996769 | , | 443 | 0.254 | 25.4 | 443 | : | 25.4 | ,
166 | 2.200000 | 166 |  | 615 | 71.8 |  | 615 | 69.847537 |  | 71.61600128 | 615 | : | 71.616001 | , | 444 | 0.283 | 28.3 | 444 | : | 28.3 | ,
167 | 2.200000 | 167 |  | 620 | 62.9773736 |  | 620 | 61.0249106 |  | 62.5699955 | 620 | : | 62.569995 | , | 445 | 0.315 | 31.5 | 445 | : | 31.5 | ,
168 | 2.200000 | 168 |  | 625 | 55.06140989 |  | 625 | 53.10894689 |  | 54.45360813 | 625 | : | 54.453608 | , | 446 | 0.345 | 34.5 | 446 | : | 34.5 | ,
169 | 2.400000 | 169 |  | 630 | 49.9 |  | 630 | 47.947537 |  | 49.16151691 | 630 | : | 49.161517 | , | 447 | 0.383 | 38.3 | 447 | : | 38.3 | ,
170 | 2.200000 | 170 |  | 635 | 45.12246045 |  | 635 | 43.16999745 |  | 44.26301521 | 635 | : | 44.263015 | , | 448 | 0.433 | 43.3 | 448 | : | 43.3 | ,
171 | 2.200000 | 171 |  | 640 | 41.09204659 |  | 640 | 39.13958359 |  | 40.13055562 | 640 | : | 40.130556 | , | 449 | 0.48 | 48 | 449 | : | 48 | ,
172 | 2.100000 | 172 |  | 645 | 37.512914 |  | 645 | 35.560451 |  | 36.46080326 | 645 | : | 36.460803 | , | 450 | 0.538 | 53.8 | 450 | : | 53.8 | ,
173 | 2.100000 | 173 |  | 650 | 34.36520977 |  | 650 | 32.41274677 |  | 33.23340255 | 650 | : | 33.233403 | , | 451 | 0.587 | 58.7 | 451 | : | 58.7 | ,
174 | 2.100000 | 174 |  | 655 | 32.17546646 |  | 655 | 30.22300346 |  | 30.9882173 | 655 | : | 30.988217 | , | 452 | 0.649 | 64.9 | 452 | : | 64.9 | ,
175 | 2.200000 | 175 |  | 660 | 29.53588495 |  | 660 | 27.58342195 |  | 28.28180444 | 660 | : | 28.281804 | , | 453 | 0.708 | 70.8 | 453 | : | 70.8 | ,
176 | 2.200000 | 176 |  | 665 | 25.98129627 |  | 665 | 24.02883327 |  | 24.63721741 | 665 | : | 24.637217 | , | 454 | 0.771 | 77.1 | 454 | : | 77.1 | ,
177 | 2.300000 | 177 |  | 670 | 22.76189837 |  | 670 | 20.80943537 |  | 21.33630782 | 670 | : | 21.336308 | , | 455 | 0.835 | 83.5 | 455 | : | 83.5 | ,
178 | 2.200000 | 178 |  | 675 | 20.14689506 |  | 675 | 18.19443206 |  | 18.65509545 | 675 | : | 18.655095 | , | 456 | 0.888 | 88.8 | 456 | : | 88.8 | ,
179 | 2.100000 | 179 |  | 680 | 17.34473171 |  | 680 | 15.39226871 |  | 15.78198435 | 680 | : | 15.781984 | , | 457 | 0.934 | 93.4 | 457 | : | 93.4 | ,
180 | 2.000000 | 180 |  | 685 | 15.23842244 |  | 685 | 13.28595944 |  | 13.6223456 | 685 | : | 13.622346 | , | 458 | 0.978 | 97.8 | 458 | : | 97.8 | ,
181 | 2.000000 | 181 |  | 690 | 13.97522283 |  | 690 | 12.02275983 |  | 12.32716314 | 690 | : | 12.327163 | , | 459 | 0.996 | 99.6 | 459 | : | 99.6 | ,
182 | 2.100000 | 182 |  | 695 | 12.42241129 |  | 695 | 10.46994829 |  | 10.73503609 | 695 | : | 10.735036 | , | 460 | 0.997 | 99.7 | 460 | : | 99.7 | ,
183 | 2.100000 | 183 |  | 700 | 10.80729562 |  | 700 | 8.854832622 |  | 9.07902743 | 700 | : | 9.079027 | , | 461 | 0.994 | 99.4 | 461 | : | 99.4 | ,
184 | 2.100000 | 184 |  | 705 | 9.56594867 |  | 705 | 7.613485672 |  | 7.806250915 | 705 | : | 7.806251 | , | 462 | 0.972 | 97.2 | 462 | : | 97.2 | ,
185 | 2.100000 | 185 |  | 710 | 8.06426226 |  | 710 | 6.111799262 |  | 6.266543425 | 710 | : | 6.266543 | , | 463 | 0.94 | 94 | 463 | : | 94 | ,
186 | 2.100000 | 186 |  | 715 | 6.82421389 |  | 715 | 4.871750892 |  | 4.995098368 | 715 | : | 4.995098 | , | 464 | 0.896 | 89.6 | 464 | : | 89.6 | ,
187 | 2.100000 | 187 |  | 720 | 5.67732774 |  | 720 | 3.724864742 |  | 3.819174298 | 720 | : | 3.819174 | , | 465 | 0.843 | 84.3 | 465 | : | 84.3 | ,
188 | 2.100000 | 188 |  | 725 | 4.23954306 |  | 725 | 2.287080062 |  | 2.344986461 | 725 | : | 2.344986 | , | 466 | 0.8 | 80 | 466 | : | 80 | ,
189 | 2.200000 | 189 |  | 730 | 3.52889436 |  | 730 | 1.576431362 |  | 1.616344903 | 730 | : | 1.616345 | , | 467 | 0.738 | 73.8 | 467 | : | 73.8 | ,
190 | 2.300000 | 190 |  | 735 | 2.98427309 |  | 735 | 1.031810092 |  | 1.05793441 | 735 | : | 1.057934 | , | 468 | 0.687 | 68.7 | 468 | : | 68.7 | ,
191 | 2.300000 | 191 |  | 740 | 2.57768389 |  | 740 | 0.6252208917 |  | 0.6410508102 | 740 | : | 0.641051 | , | 469 | 0.644 | 64.4 | 469 | : | 64.4 | ,
192 | 2.300000 | 192 |  | 745 | 2.59020604 |  | 745 | 0.6377430417 |  | 0.6538900075 | 745 | : | 0.653890 | , | 470 | 0.597 | 59.7 | 470 | : | 59.7 | ,
193 | 2.200000 | 193 |  | 750 | 2.50634585 |  | 750 | 0.5538828517 |  | 0.567906568 | 750 | : | 0.567907 | , | 471 | 0.56 | 56 | 471 | : | 56 | ,
194 | 2.100000 | 194 |  | 755 | 2.47091866 |  | 755 | 0.5184556617 |  | 0.5315823997 | 755 | : | 0.531582 | , | 472 | 0.527 | 52.7 | 472 | : | 52.7 | ,
195 | 2.000000 | 195 |  | 760 | 2.59607357 |  | 760 | 0.6436105717 |  | 0.659906097 | 760 | : | 0.659906 | , | 473 | 0.497 | 49.7 | 473 | : | 49.7 | ,
196 | 2.000000 | 196 |  | 765 | 2.59779063 |  | 765 | 0.6453276317 |  | 0.6616666311 | 765 | : | 0.661667 | , | 474 | 0.474 | 47.4 | 474 | : | 47.4 | ,
197 | 2.100000 | 197 |  | 770 | 2.40077885 |  | 770 | 0.4483158517 |  | 0.4596667254 | 770 | : | 0.459667 | , | 475 | 0.449 | 44.9 | 475 | : | 44.9 | ,
198 | 2.100000 | 198 |  | 775 | 2.49478362 |  | 775 | 0.5423206217 |  | 0.5560515948 | 775 | : | 0.556052 | , | 476 | 0.429 | 42.9 | 476 | : | 42.9 | ,
199 | 2.200000 | 199 |  | 780 | 2.28113536 |  | 780 | 0.3286723617 |  | 0.3369939913 | 780 | : | 0.336994 | , | 477 | 0.407 | 40.7 | 477 | : | 40.7 | ,
200 | 2.000000 | 200 |  | 785 | 2.09084568 |  | 785 | 0.1383826817 |  | 0.1418863819 | 785 | : | 0.141886 | , | 478 | 0.385 | 38.5 | 478 | : | 38.5 | ,
201 | 2.000000 | 201 |  | 790 | 2.19392596 |  | 790 | 0.2414629617 |  | 0.2475765434 | 790 | : | 0.247577 | , | 479 | 0.367 | 36.7 | 479 | : | 36.7 | ,
202 | 2.000000 | 202 |  | 795 | 1.99931401 |  | 795 | 0 |  | 0 | 795 | : | 0.000000 | , | 480 | 0.347 | 34.7 | 480 | : | 34.7 | ,
203 | 2.000000 | 203 |  | 800 | 1.93515397 |  | 800 | 0 |  | 0 | 800 | : | 0.000000 | , | 481 | 0.328 | 32.8 | 481 | : | 32.8 | ,
204 | 2.100000 | 204 |  | 805 | 2.10106285 |  | 805 | 0 |  | 0 | 805 | : | 0.000000 | , | 482 | 0.313 | 31.3 | 482 | : | 31.3 | ,
205 | 2.200000 | 205 |  | 810 | 1.98822737 |  | 810 | 0 |  | 0 | 810 | : | 0.000000 | , | 483 | 0.291 | 29.1 | 483 | : | 29.1 | ,
206 | 2.200000 | 206 |  | 815 | 1.99844345 |  | 815 | 0 |  | 0 | 815 | : | 0.000000 | , | 484 | 0.277 | 27.7 | 484 | : | 27.7 | ,
207 | 2.200000 | 207 |  | 820 | 1.99571662 |  | 820 | 0 |  | 0 | 820 | : | 0.000000 | , | 485 | 0.26 | 26 | 485 | : | 26 | ,
208 | 2.100000 | 208 |  | 825 | 1.90387025 |  | 825 | 0 |  | 0 | 825 | : | 0.000000 | , | 486 | 0.248 | 24.8 | 486 | : | 24.8 | ,
209 | 2.000000 | 209 |  | 830 | 1.84982625 |  | 830 | 0 |  | 0 | 830 | : | 0.000000 | , | 487 | 0.236 | 23.6 | 487 | : | 23.6 | ,
210 | 2.100000 | 210 |  | 1200 | 1.84982625 |  | 1200 | 0 |  | 0 | 1200 | : | 0.000000 | , | 488 | 0.223 | 22.3 | 488 | : | 22.3 | ,
211 | 2.000000 | 211 |  |  |  |  |  |  |  |  |  |  |  |  | 489 | 0.217 | 21.7 | 489 | : | 21.7 | ,
212 | 2.000000 | 212 |  |  |  |  |  |  |  |  |  |  |  |  | 490 | 0.212 | 21.2 | 490 | : | 21.2 | ,
213 | 2.000000 | 213 |  |  |  |  |  |  |  |  |  |  |  |  | 491 | 0.201 | 20.1 | 491 | : | 20.1 | ,
214 | 2.200000 | 214 |  |  |  |  |  |  |  |  |  |  |  |  | 492 | 0.194 | 19.4 | 492 | : | 19.4 | ,
215 | 2.100000 | 215 |  |  |  |  |  |  |  |  |  |  |  |  | 493 | 0.191 | 19.1 | 493 | : | 19.1 | ,
216 | 2.100000 | 216 |  |  |  |  |  |  |  |  |  |  |  |  | 494 | 0.187 | 18.7 | 494 | : | 18.7 | ,
217 | 2.200000 | 217 |  |  |  |  |  |  |  |  |  |  |  |  | 495 | 0.185 | 18.5 | 495 | : | 18.5 | ,
218 | 2.300000 | 218 |  |  |  |  |  |  |  |  |  |  |  |  | 496 | 0.182 | 18.2 | 496 | : | 18.2 | ,
219 | 2.200000 | 219 |  |  |  |  |  |  |  |  |  |  |  |  | 497 | 0.178 | 17.8 | 497 | : | 17.8 | ,
220 | 2.200000 | 220 |  |  |  |  |  |  |  |  |  |  |  |  | 498 | 0.178 | 17.8 | 498 | : | 17.8 | ,
221 | 2.300000 | 221 |  |  |  |  |  |  |  |  |  |  |  |  | 499 | 0.174 | 17.4 | 499 | : | 17.4 | ,
222 | 2.300000 | 222 |  |  |  |  |  |  |  |  |  |  |  |  | 500 | 0.175 | 17.5 | 500 | : | 17.5 | ,
223 | 2.200000 | 223 |  |  |  |  |  |  |  |  |  |  |  |  | 501 | 0.177 | 17.7 | 501 | : | 17.7 | ,
224 | 2.000000 | 224 |  |  |  |  |  |  |  |  |  |  |  |  | 502 | 0.179 | 17.9 | 502 | : | 17.9 | ,
225 | 2.100000 | 225 |  |  |  |  |  |  |  |  |  |  |  |  | 503 | 0.177 | 17.7 | 503 | : | 17.7 | ,
226 | 2.000000 | 226 |  |  |  |  |  |  |  |  |  |  |  |  | 504 | 0.18 | 18 | 504 | : | 18 | ,
227 | 2.000000 | 227 |  |  |  |  |  |  |  |  |  |  |  |  | 505 | 0.185 | 18.5 | 505 | : | 18.5 | ,
228 | 2.000000 | 228 |  |  |  |  |  |  |  |  |  |  |  |  | 506 | 0.188 | 18.8 | 506 | : | 18.8 | ,
229 | 2.100000 | 229 |  |  |  |  |  |  |  |  |  |  |  |  | 507 | 0.194 | 19.4 | 507 | : | 19.4 | ,
230 | 2.100000 | 230 |  |  |  |  |  |  |  |  |  |  |  |  | 508 | 0.193 | 19.3 | 508 | : | 19.3 | ,
231 | 2.000000 | 231 |  |  |  |  |  |  |  |  |  |  |  |  | 509 | 0.201 | 20.1 | 509 | : | 20.1 | ,
232 | 2.000000 | 232 |  |  |  |  |  |  |  |  |  |  |  |  | 510 | 0.206 | 20.6 | 510 | : | 20.6 | ,
233 | 2.000000 | 233 |  |  |  |  |  |  |  |  |  |  |  |  | 511 | 0.209 | 20.9 | 511 | : | 20.9 | ,
234 | 2.000000 | 234 |  |  |  |  |  |  |  |  |  |  |  |  | 512 | 0.22 | 22 | 512 | : | 22 | ,
235 | 2.100000 | 235 |  |  |  |  |  |  |  |  |  |  |  |  | 513 | 0.225 | 22.5 | 513 | : | 22.5 | ,
236 | 2.100000 | 236 |  |  |  |  |  |  |  |  |  |  |  |  | 514 | 0.23 | 23 | 514 | : | 23 | ,
237 | 2.200000 | 237 |  |  |  |  |  |  |  |  |  |  |  |  | 515 | 0.238 | 23.8 | 515 | : | 23.8 | ,
238 | 2.100000 | 238 |  |  |  |  |  |  |  |  |  |  |  |  | 516 | 0.243 | 24.3 | 516 | : | 24.3 | ,
239 | 2.000000 | 239 |  |  |  |  |  |  |  |  |  |  |  |  | 517 | 0.251 | 25.1 | 517 | : | 25.1 | ,
240 | 2.000000 | 240 |  |  |  |  |  |  |  |  |  |  |  |  | 518 | 0.254 | 25.4 | 518 | : | 25.4 | ,
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

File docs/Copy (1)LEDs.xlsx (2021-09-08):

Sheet: LEDs
1 W = 1000 mW
1 mW = 1000 µW
1 Quadratzentimeter = 100 Quadratmillimeter
1 Quadratmeter = 10000 Quadratzentimeter | 0.5856515373
1 mW/m² = 0,1 µW/ cm² oder
1 µW/cm² =10 mW/m² |  | http://zeiss-campus.magnet.fsu.edu/articles/lightsources/leds.html
8.9 µW/mm² |  |  |  |  |  | LED | RGB LED | Laser
 |  |  |  |  |  | λP |  |  |  | Δλ | λB | Ø |  |  |  |  | 2θ1/2 |  | ΦV | IV | ΦV | PD | IF | VF | VF | VF | VF | VF | IF
 |  |  |  |  |  | IF = 15 mA |  |  |  | IF = 15 mA |  |  |  |  |  |  |  |  |  |  | IF = 15 mA |  |  |  |  |  | IF = 12 mA | 3.3 | 12 |  | 6.0 | 12.0
 |  |  |  |  |  | [nm] |  |  |  | [nm] | [nm] | [mm] | [mm] | [mm] |  |  | [o] | [lm/W] | [lm] | [mcd] | [mW] | [mW] | [mA] | [V] | [V] | [V] | [V] | [V] | [mA] | [Ω] |  |  |  | [Ω]
 |  | Product | Shop | Light color | Material | Peak Emmision Wavelength | Column1 | Column2 | No | Spectrum Half Width | FWHM Bandwidth | Diameter | Column3 | Length | Long Leg | Lens Color | Viewing Angle | Effizienz | Luminous flux | Luminous Intensity | Radiant Flux | Power Dissipation | Forward Current | Forward Voltage Min | Forward Voltage Max | Forward Voltage Typ. | Forward Voltage | GPIO | Column4 | Calculated series resistor | Column7 | Column6 | Column5 | Series resistor
 |  | Nichia NSPU510CS (https://www.nichia.co.jp/specification/products/led/NSPU510CS-E.pdf) |  | UV |  | 375 |  |  | 1 | 10 | 370-380 | 5 | 5.3 | 8.3 | Anode (+) | Water Clear | 40 |  |  |  | 15.1 | 80 | 20 | 2.90 | 4.00 | 3.30 | 3.25 | 12 |  | 4.2 | 225.0 |  |  | 4.3 - 5.0 | 4 | 1 | 0
 |  | LL-504UVAC2E-Q5C |  | UV |  | 395 |  |  | 2 | 40 | 375-415 | 5 | 5.85 | 8.65 | Anode (+) | Water Clear | 15 |  |  | 350 |  |  |  |  |  |  |  | 13 |  | 275.0 | 500.0 |  |  |  | 5 |  | 1 | TX
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

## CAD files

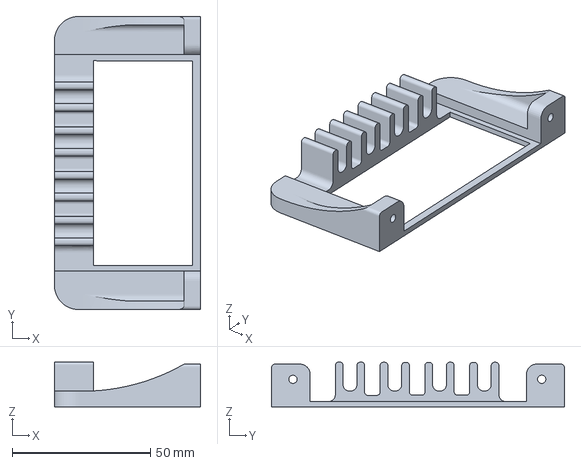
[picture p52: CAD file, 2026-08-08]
setup/case/3d-printing/Anycubic-Kobra-S1/ACE-Pro-Buffer-Bay/ace-pro-buffer-bay.3mf
52.9 x 106.0 x 16.3 mm

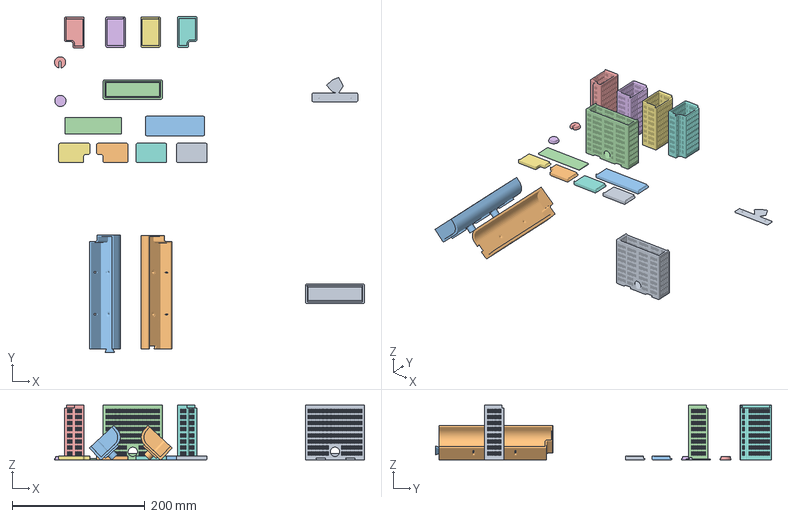
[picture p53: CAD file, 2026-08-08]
setup/case/3d-printing/Anycubic-Kobra-S1/ACE-Pro-Filament-Guide-and-Drybox/AcePro_Drybox_Filamentguide_v4.3.2_ABS_BL.3mf
466.5 x 505.5 x 82.1 mm
AcePro_Logo_v4.3.1.stl
Filamentguide right v4.0.0
Filamentguide left v4.0.0
Drybox Middle Frame v4.2.0
Drybox Middle Cable Lid v2.0.0
Drybox Middle NoCable v2.0.0
Drybox 1 Lid v4.3.1
Drybox 2 Lid v4.3.1
Drybox 3 Lid v4.3.1
Drybox 4 Lid v4.3.1
Drybox Middle Lid v4.3.2
Drybox Middle v4.3.2
Drybox 1 v4.3.2
Drybox 2 v4.3.2
Drybox 3 v4.3.2
Drybox 4 v4.3.2
Drybox_Middle_v4.3.1.stl

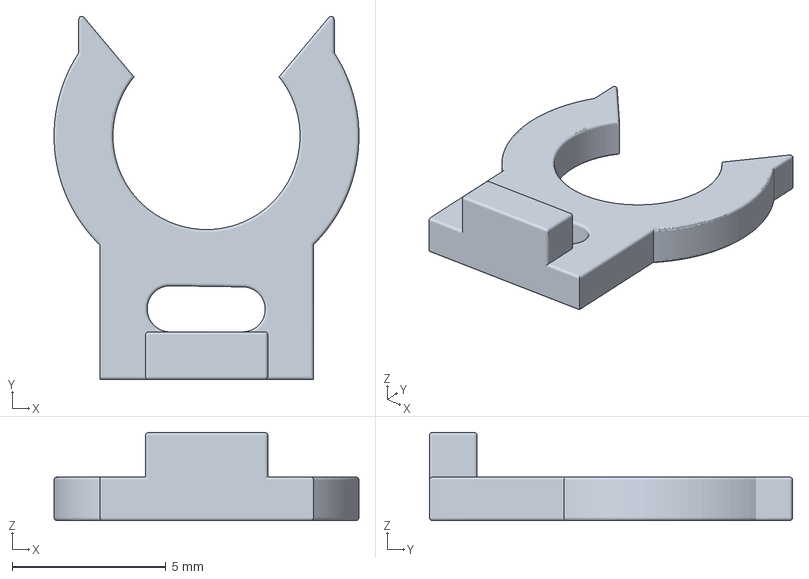
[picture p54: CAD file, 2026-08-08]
setup/case/3d-printing/Anycubic-Kobra-S1/ACE-Pro-Klemm-Finger/1.3mf
9.93 x 11.8 x 2.87 mm

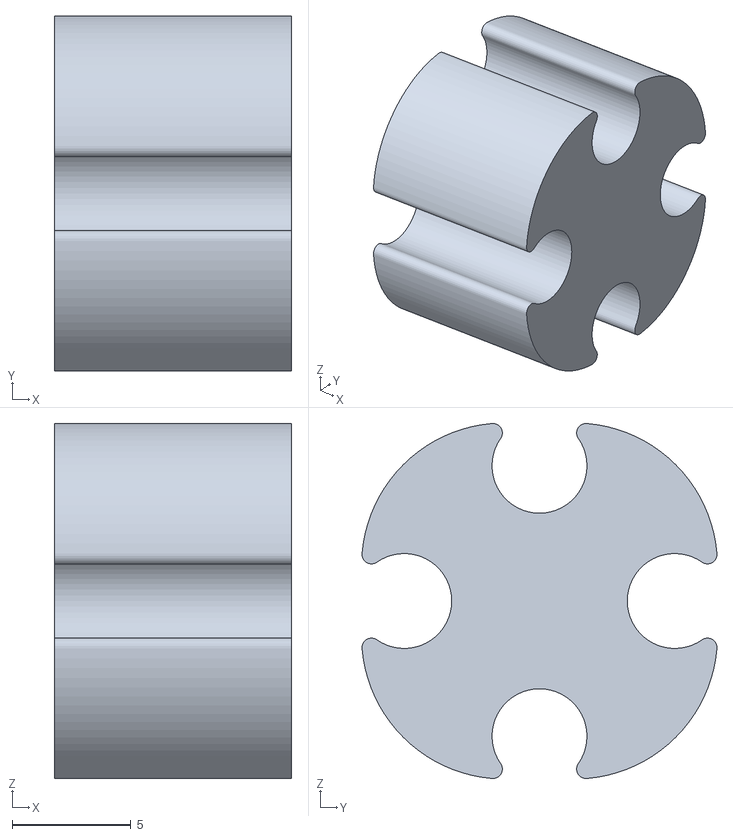
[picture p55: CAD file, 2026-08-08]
setup/case/3d-printing/Anycubic-Kobra-S1/ACE-Pro-PTFE/ptfe joiner.stl
10.0 x 15.0 x 15.0

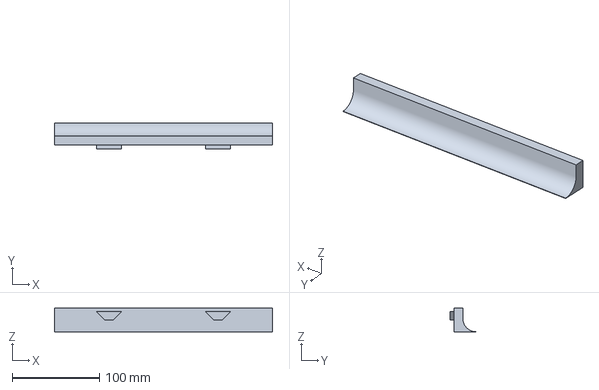
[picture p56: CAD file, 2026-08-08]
setup/case/3d-printing/Anycubic-Kobra-S1/Short+Universal+Anycubic+ACE+Pro+Riser+with+Skadis/S1C Adapter Left.3mf
249.9 x 29.8 x 27.5 mm

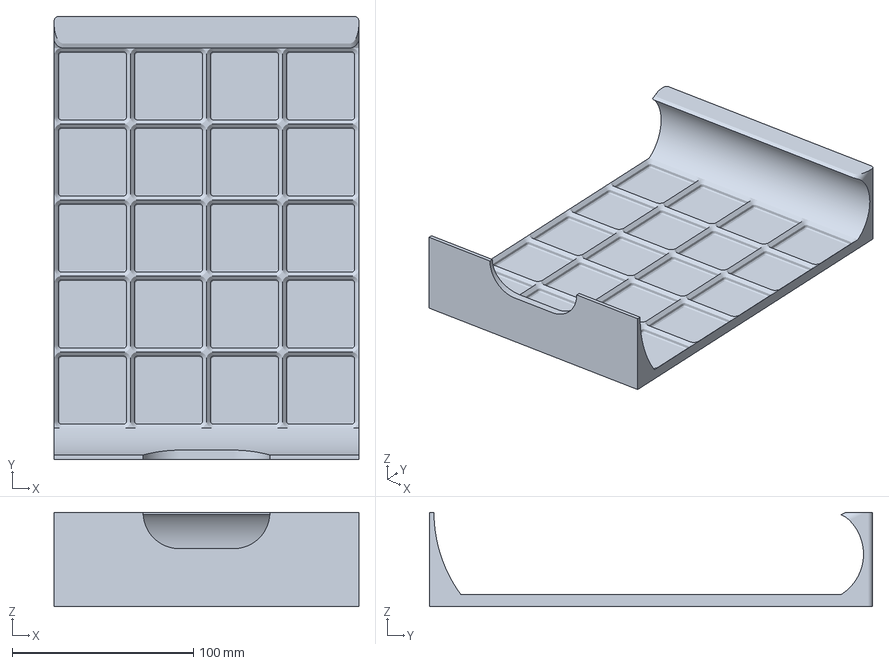
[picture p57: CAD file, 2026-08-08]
setup/case/3d-printing/Anycubic-Kobra-S1/Universal+Anycubic+ACE+Pro+Riser+with+Skadis+Board/The upper Riser tray - Gridfinity - BBL.3mf
168.4 x 244.7 x 52.0 mm

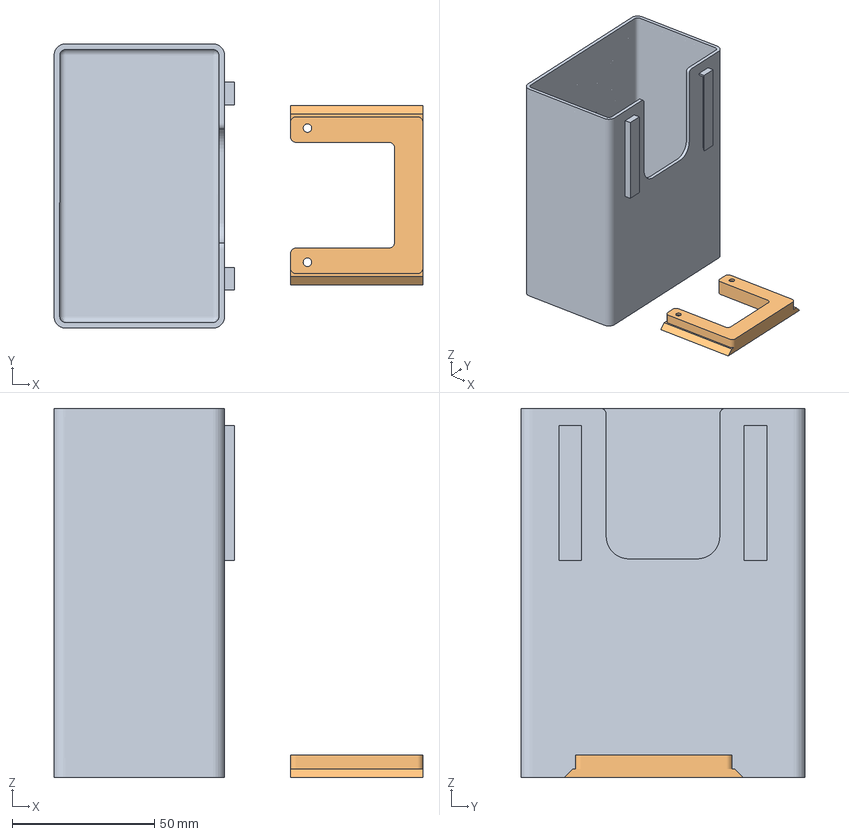
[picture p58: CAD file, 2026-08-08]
setup/case/3d-printing/Anycubic-Kobra-S1/Wastebucket/cobra-s1-wastebucket-no-holes.3mf
129.8 x 100.0 x 130.0 mm
Bin
Secure.stl

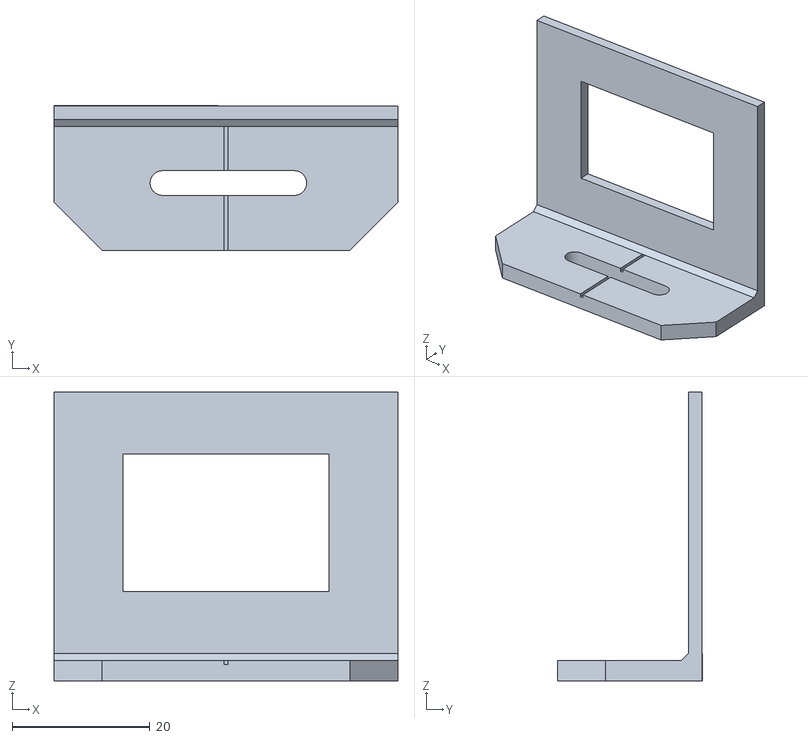
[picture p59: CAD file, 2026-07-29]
setup/case/3d-printing/grating-Spectrometer/grating-Spectrometer-Grating-Holder.stl
50.0 x 21.1 x 42.0

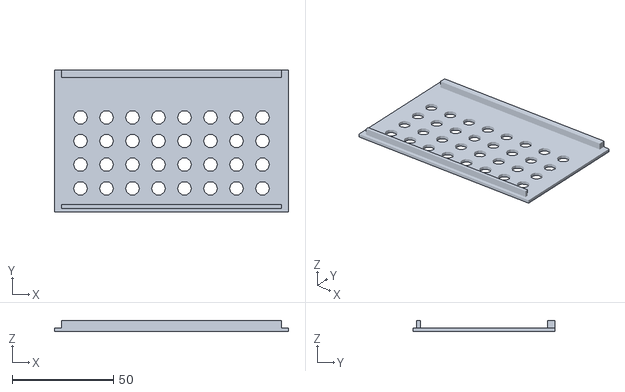
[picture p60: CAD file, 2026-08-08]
setup/case/3d-printing/smart-LED-Array-LED-Holder-for-12x14cm-Case.stl
115.4 x 70.0 x 5.40

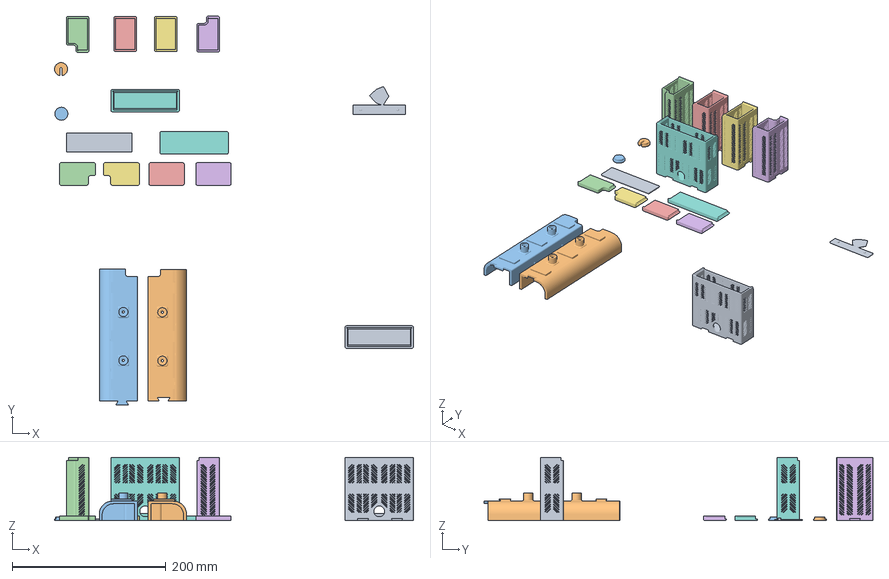
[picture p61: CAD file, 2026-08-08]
setup/case/3d-printing/Anycubic-Kobra-S1/ACE-Pro-Filament-Guide-and-Drybox/AcePro_Drybox_Filamentguide_v4.3.1_PETG_BL.3mf
466.5 x 505.5 x 82.1 mm
Drybox Middle Frame v4.2.0
Drybox Middle Cable Lid v2.0.0
Drybox Middle NoCable v2.0.0
Drybox 1 Lid v4.3.1
Drybox 2 Lid v4.3.1
Drybox 3 Lid v4.3.1
Drybox 4 Lid v4.3.1
Drybox Middle Lid v4.3.1
AcePro_Logo_v4.3.1.stl
Filamentguide right v4.0.0
Filamentguide left v4.0.0
Drybox 1 v4.3.1
Drybox 2 v4.3.1
Drybox 4 v4.3.1
Drybox 3 v4.3.1
Drybox Middle v4.3.1
Drybox_Middle_v4.3.1.stl

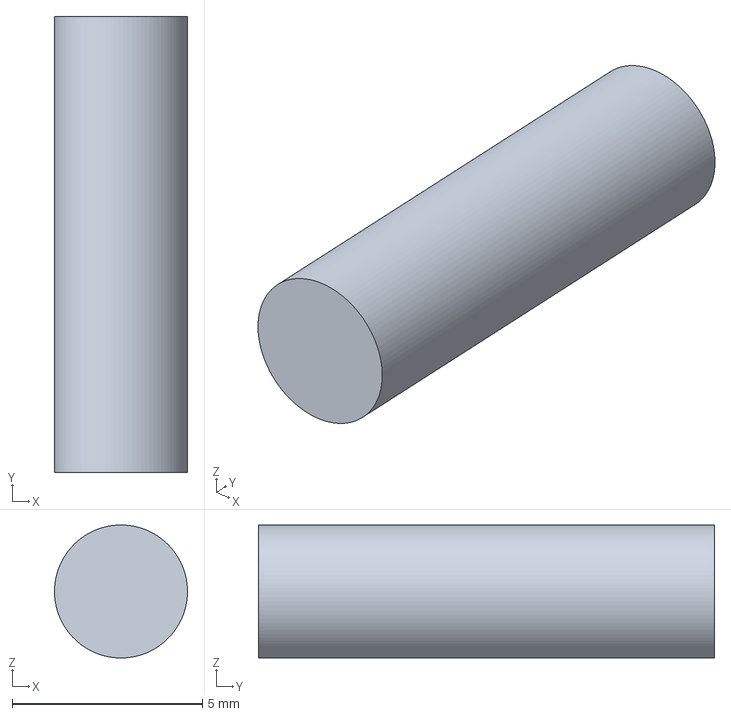
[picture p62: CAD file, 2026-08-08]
setup/case/3d-printing/Anycubic-Kobra-S1/Short+Universal+Anycubic+ACE+Pro+Riser+with+Skadis/The Riser Plug - BBL.3mf
3.50 x 12.0 x 3.50 mm

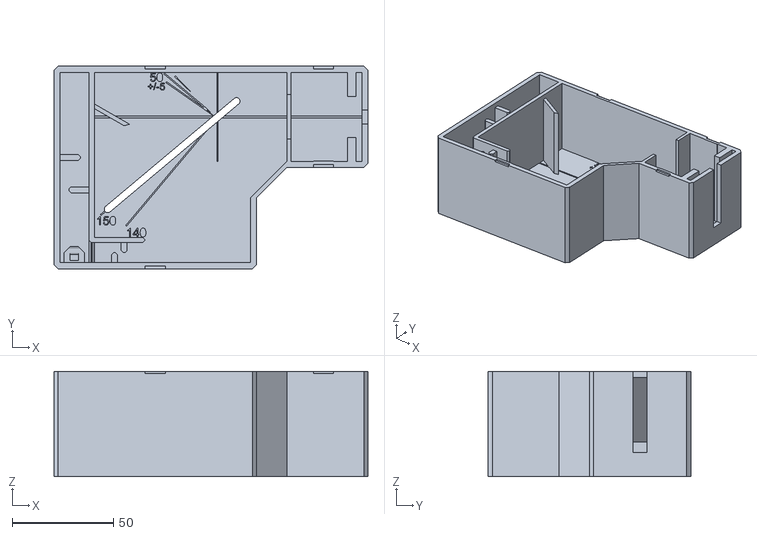
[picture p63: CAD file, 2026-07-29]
setup/case/3d-printing/grating-Spectrometer/grating-Spectrometer-Short-Case.stl
155.0 x 100.0 x 52.0

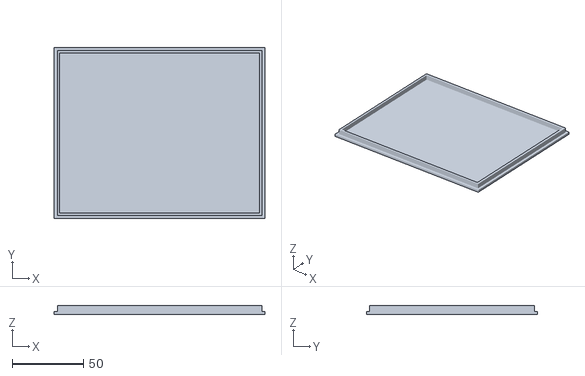
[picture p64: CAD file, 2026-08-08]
setup/case/3d-printing/smart-LED-Array-Lid-for-12x14cm-Case.stl
148.0 x 120.0 x 6.00

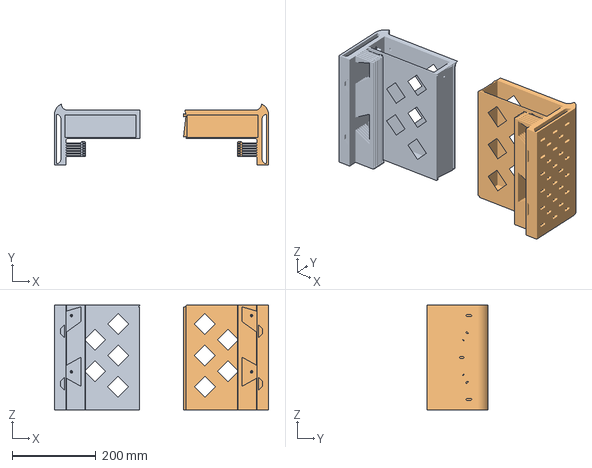
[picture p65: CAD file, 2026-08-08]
setup/case/3d-printing/Anycubic-Kobra-S1/Short+Universal+Anycubic+ACE+Pro+Riser+with+Skadis/The+universal+short+Riser+V2+-+BBL.3mf
510.6 x 145.1 x 249.9 mm
The short Riser part Left V2
The short Riser part Right V2

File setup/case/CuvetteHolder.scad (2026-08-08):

/*

smart-LED-Array
smart-Grating-Spectrometer
smart-UV-Photometer
smart-Colorimeter
smart-RGB-Photometer
smart-IR-Turbidimeter

OpenSCAD 3D model
Version 0.3

smart-LED-Array © Copyright 2020 - 2026 by smartAquaMetering. All Rights Reserved.
smart-Grating-Spectrometer © Copyright 2020 - 2026 by smartAquaMetering. All Rights Reserved.
smart-UV-Photometer © Copyright 2020 - 2026 by smartAquaMetering. All Rights Reserved.
smart-Colorimeter © Copyright 2020 - 2026 by smartAquaMetering. All Rights Reserved.
smart-RGB-Photometer © Copyright 2020 - 2026 by smartAquaMetering. All Rights Reserved.
smart-IR-Turbidimeter © Copyright 2020 - 2026 by smartAquaMetering. All Rights Reserved.

https://github.com/smartaquametering
https://github.com/smartaquametering/smartPhotometer

smart-LED-Array by smartAquaMetering is licensed under a Creative Commons Attribution-ShareAlike 4.0 International License.
smart-Grating-Spectrometer by smartAquaMetering is licensed under a Creative Commons Attribution-ShareAlike 4.0 International License.
smart-UV-Photometer by smartAquaMetering is licensed under a Creative Commons Attribution-ShareAlike 4.0 International License.
smart-Colorimeter by smartAquaMetering is licensed under a Creative Commons Attribution-ShareAlike 4.0 International License.
smart-RGB-Photometer by smartAquaMetering is licensed under a Creative Commons Attribution-ShareAlike 4.0 International License.
smart-IR-Turbidimeter by smartAquaMetering is licensed under a Creative Commons Attribution-ShareAlike 4.0 International License.

Based on a work at https://github.com/smartaquametering/smartPhotometer.
Permissions beyond the scope of this license may be available at https://github.com/smartaquametering/smartPhotometer/blob/main/LICENSE.

View terms of the license here:
http://creativecommons.org/licenses/by-sa/4.0/

Version history
---------------
0.3 2026-08-02 Improve Description and Dokumentation.
0.2 2020-11-23 Translation into English.
0.1 2020-10-25 Initial release.

*/

// ---------------------------------------------------------------------------------------------------------------------------
// smart-UV-Photometer
// ---------------------------------------------------------------------------------------------------------------------------
// - smartAquaMetering-Case + Cuvette, LED(s) and sensor holder
// - UV-LED beam angle    : 180 Degree (Absorbance measurement)
// - UV-Sensor            : VEML6070

//sysmode  = 1;                                 // smart-UV-Photometer-Case
  sys11    = "UV-LED";                          // Labeling back side
  sys12    = "Photometer";
  sys13    = "Transmitted light";
  sys14    = "";                                // Labeling left side
  sys15    = "";
  sys16    = "";

// ---------------------------------------------------------------------------------------------------------------------------
// smart-Colorimeter
// ---------------------------------------------------------------------------------------------------------------------------
// - smartAquaMetering-Case + MC, Cuvette, LED(s) and sensor holders
// - RGB-LED beam angle   : 180 Degree (Absorbance measurement)
// - RGB-Sensor           : Adafruit TCS34725

//sysmode  = 2;                                 // smart-Colorimeter-Case
  sys21    = "Warm-White-LED";                  // Labeling back side
  sys22    = "Colorimeter";
  sys23    = "Transmitted light";
  sys24    = "";                                // Labeling left side
  sys25    = "";
  sys26    = "";

// ---------------------------------------------------------------------------------------------------------------------------
// smart-RGB-Photometer
// ---------------------------------------------------------------------------------------------------------------------------
// - smartAquaMetering-Case + MC, Cuvette, LED(s) and sensor holders
// - RGB-LED beam angle   : 180 Degree (Absorbance measurement)
// - IR-LED beam angle    : 90 Degree (Nephelometric turbidity measurement)
// - VIS and IR Sensor    : Adafruit TSL2591

//sysmode  = 3;                                 // smart-RGB-Photometer-Case
  sys31    = "RGB-LED";                         // Labeling back side
  sys32    = "Photometer";
  sys33    = "Transmitted light";
  sys34    = "IR-LED";                          // Labeling left side
  sys35    = "Turbidimeter";
  sys36    = "Scattered light";

// ---------------------------------------------------------------------------------------------------------------------------
// smart-IR-Turbidimeter
// ---------------------------------------------------------------------------------------------------------------------------
// - smartAquaMetering-Case + MC, Cuvette, LED(s) and sensor holders
// - IR-LED beam angle    : 180 Degree (Absorbance measurement)
// - IR-LED beam angle    : 90 Degree (Nephelometric turbidity measurement)
// - IR Sensor            : Adafruit TSL2591

//sysmode  = 4;                                 // smart-IR-Turbidimeter-Case
  sys41    = "IR-LED";                          // Labeling back side
  sys42    = "Photometer";
  sys43    = "Transmitted light";
  sys44    = "IR-LED";                          // Labeling left side
  sys45    = "Turbidimeter";
  sys46    = "Scattered light";

// ---------------------------------------------------------------------------------------------------------------------------
// smart-Cuvette-Holder
// ---------------------------------------------------------------------------------------------------------------------------
// - Beam angle           : 180 Degree (Absorbance measurement)
// - Toslink connectors   : 2x

//sysmode  = 5;                                 // smart-Cuvette-Holder
  sys51    = "";                                // Labeling back side
  sys52    = "";
  sys53    = "";
  sys54    = "";                                // Labeling left side
  sys55    = "";
  sys56    = "";

// ---------------------------------------------------------------------------------------------------------------------------
// smartAquaMetering-Case-Lid
// ---------------------------------------------------------------------------------------------------------------------------
//sysmode  = 11;                                // smartAquaMetering-Case-Lid

// ---------------------------------------------------------------------------------------------------------------------------
// smartAquaMetering-Cover-for-square-Cuvette
// ---------------------------------------------------------------------------------------------------------------------------
//sysmode  = 12;                                // smart-Photometer-Cover-for-square-Cuvette

// ---------------------------------------------------------------------------------------------------------------------------
// smartAquaMetering-Cover-for-round-Cuvette
// ---------------------------------------------------------------------------------------------------------------------------
//sysmode  = 13;                                // smart-Photometer-Cover-for-round-Cuvette

// ---------------------------------------------------------------------------------------------------------------------------
// smart-Grating-Spectrometer-Grating-Holder
// ---------------------------------------------------------------------------------------------------------------------------
//sysmode  = 14;                                // smart-Grating-Spectrometer-Grating-Holder

// ---------------------------------------------------------------------------------------------------------------------------
// smart-Grating-Spectrometer-USB-Camera-Holder
// ---------------------------------------------------------------------------------------------------------------------------
//sysmode  = 15;                                // smart-Grating-Spectrometer-USB-Camera-Holder

// ---------------------------------------------------------------------------------------------------------------------------
// smart-Grating-Spectrometer-Lightslit-Cuvette-Holder
// ---------------------------------------------------------------------------------------------------------------------------
//sysmode  = 16;                                // smart-Grating-Spectrometer-Lightslit-Cuvette-Holder

// ---------------------------------------------------------------------------------------------------------------------------
// smart-Grating-Spectrometer-Case
// ---------------------------------------------------------------------------------------------------------------------------
//sysmode  = 17;                                // smart-Grating-Spectrometer-Case Part 1
//sysmode  = 18;                                // smart-Grating-Spectrometer-Case Part 2
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

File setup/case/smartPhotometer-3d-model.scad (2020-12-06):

/*

smart-UV-Photometer
smart-Colorimeter
smart-RGB-Photometer
smart-IR-Turbidimeter

OpenSCAD 3D model
Version 0.2

smart-UV-Photometer © Copyright 2020 by smartAquaMetering. All Rights Reserved.
smart-Colorimeter © Copyright 2020 by smartAquaMetering. All Rights Reserved.
smart-RGB-Photometer © Copyright 2020 by smartAquaMetering. All Rights Reserved.
smart-IR-Turbidimeter © Copyright 2020 by smartAquaMetering. All Rights Reserved.

https://github.com/smartaquametering
https://github.com/smartaquametering/smartPhotometer

smart-UV-Photometer by smartAquaMetering is licensed under a Creative Commons Attribution-ShareAlike 4.0 International License.
smart-Colorimeter by smartAquaMetering is licensed under a Creative Commons Attribution-ShareAlike 4.0 International License.
smart-RGB-Photometer by smartAquaMetering is licensed under a Creative Commons Attribution-ShareAlike 4.0 International License.
smart-IR-Turbidimeter by smartAquaMetering is licensed under a Creative Commons Attribution-ShareAlike 4.0 International License.

Based on a work at https://github.com/smartaquametering/smartPhotometer.
Permissions beyond the scope of this license may be available at https://github.com/smartaquametering/smartPhotometer/blob/main/LICENSE.

View terms of the license here:
http://creativecommons.org/licenses/by-sa/4.0/

Version history
---------------
0.2 2020-11-23 Translation into English.
0.1 2020-10-25 Initial release.

*/

// -------------------------------------------------------------------------
// smart-UV-Photometer
// -------------------------------------------------------------------------
// - UV-LED beam angle		: 180 Degree (Absorbance measurement)
// - UV-Sensor			: VEML6070

//sysmode = 1;									// UV-LED Photometer
	sys11 = "UV-LED";							// Labeling back side
	sys12 = "Photometer";
	sys13 = "Transmitted light";
	sys14 = "";								// Labeling left side
	sys15 = "";
	sys16 = "";

// -------------------------------------------------------------------------
// smart-Colorimeter
// -------------------------------------------------------------------------
// - RGB-LED beam angle		: 180 Degree (Absorbance measurement)
// - RGB-Sensor			: Adafruit TCS34725

//sysmode = 2;									// Colorimeter
	sys21 = "RGB-LED";							// Labeling back side
	sys22 = "Photometer";
	sys23 = "Transmitted light";
	sys24 = "";								// Labeling left side
	sys25 = "";
	sys26 = "";

// -------------------------------------------------------------------------
// smart-RGB-Photometer
// -------------------------------------------------------------------------
// - RGB-LED beam angle		: 180 Degree (Absorbance measurement)
// - IR-LED beam angle		:  90 Degree (Nephelometric turbidity measurement)
// - VIS and IR Sensor		: Adafruit TSL2591

sysmode = 3;									// RGB-LED Photometer
	sys31 = "RGB-LED";							// Labeling back side
	sys32 = "Photometer";
	sys33 = "Transmitted light";
	sys34 = "IR-LED";							// Labeling left side
	sys35 = "Turbidimeter";
	sys36 = "Scattered light";

// -------------------------------------------------------------------------
// smart-IR-Turbidimeter
// -------------------------------------------------------------------------
// - IR-LED beam angle		: 180 Degree (Absorbance measurement)
// - IR-LED beam angle		:  90 Degree (Nephelometric turbidity measurement)
// - IR Sensor			: Adafruit TSL2591

//sysmode = 4;									// IR-LED Turbidimeter
	sys41 = "IR-LED";							// Labeling back side
	sys42 = "Photometer";
	sys43 = "Transmitted light";
	sys44 = "IR-LED";							// Labeling left side
	sys45 = "Turbidimeter";
	sys46 = "Scattered light";

// -------------------------------------------------------------------------
// smartPhotometer-Case-Lid
// -------------------------------------------------------------------------
//sysmode = 11;									// Case lid

// -------------------------------------------------------------------------
// smartPhotometer-Cover-for-square-Cuvette
// -------------------------------------------------------------------------
//sysmode = 12;									// Cover for square cuvette

// -------------------------------------------------------------------------
// smartPhotometer-Cover-for-round-Cuvette
// -------------------------------------------------------------------------
//sysmode = 13;								    // Cover for round cuvette

// -------------------------------------------------------------------------
// smartPhotometer-Case
// -------------------------------------------------------------------------
casemode = 1;                                   // Case + Cuvette holder
//casemode = 2;                                 // Cuvette holder only

// -------------------------------------------------------------------------
// Microcontroller
// -------------------------------------------------------------------------

mcbs	= "ESP32-WROOM-32 NodeMCU WLAN/WiFi";					// Labeling front side
mcip	= "192.168.4.1";							// Labeling case lid

// -------------------------------------------------------------------------
// Copyright
// -------------------------------------------------------------------------

cr1	= "Open Source";							// Labeling right side
cr2	= "Smart, simple and easy";
cr3	= "Made in Germany";

// -------------------------------------------------------------------------

// Cuvette
cvmode	= 1;				// 0:= Square cuvette , 1:= Round cuvette
//cvow	= 12.5;				// Outer edge length		(X,Y)
//cvh	= 45.0;				// Height			(Z)
cvow	= 16.0;				// Outer diameter		(X,Y)
cvh	    = 160.0;			// Height			(Z)
cvoe	=  0.6;				// Extra outer edge length / diameter

cvw	= cvow+cvoe;			// Total outer edge length / diameter

// Microcontroller
mch     = 50.0;				// Height (board, plugs and cables)	(X)
mcl     = 55.0;				// Length				(Y)
mcw     = 28.0;				// Width				(Z)
mcbh	=  6.0;				// Height (MC board only)		(Y)
mcbhl	=  2.0;				// Length of board holder
mcbbh	=  4.0;			    // Height of board base (height adjustment)

// USB port
usbw	=  8.0;				// Width	(X)
usbh	= 11.0;				// Height	(Z)
usbd	=  0.4;				// Depth	(Y)

// Sensors
sbid	= 20.0;				// Installation depth of sensor board (incl. board, plugs and cables)	(Y)

// Sensor - Adafruit TSL2591
sbh1	= 16.5;				// Height of sensor board - measured from bottom edge			(X)
sbw1	= 19.0;				// Width of sensor board - measured from side edge			(Z)
sbd1	=  3.5;				// Depth of sensor board						(Y)
scb1	=  9.4;				// Distance between center of sensor chip and board bottom edge		(X)
scr1	=  9.4;				// Distance between center of sensor chip and board right side edge	(Z)
scd1	=  4.0;				// Pinhole diameter for sensor chip

sb11	= "Sensor";			// Labeling front side
sb12	= "TSL2591";

// Sensor - Adafruit TCS34725
sbh2	= 20.3;				// Height of sensor board - measured from bottom edge			(X)
sbw2	= 20.3;				// Width of sensor board - measured from side edge			(Z)
sbd2	=  3.0;				// Depth of sensor board						(Y)
scb2	=  9.4;				// Distance between center of sensor chip and board bottom edge		(X)
scr2	= 11.5;				// Distance between center of sensor chip and board right side edge	(Z)
scd2	=  4.0;				// Pinhole diameter for sensor chip

sb21	= "Sensor";			// Labeling front side
sb22	= "TCS34725";

// Sensor - VEML6070
sbh3	= 12.0;				// Height of sensor board - measured from bottom edge			(X)
sbw3	= 13.0;				// Width of sensor board - measured from side edge			(Z)
sbd3	=  2.9;				// Depth of sensor board						(Y)
scb3	=  5.0;				// Distance between center of sensor chip and board bottom edge		(X)
scr3	=  6.5;				// Distance between center of sensor chip and board right side edge	(Z)
scd3	=  4.0;				// Pinhole diameter for sensor chip

sb31	= "Sensor";			// Labeling front side
sb32	= "VEML6070";

// LEDs
ledh	= 20.0;				// Installation height

led1l	=  8.5;				// Length
led1w	=  5.4;				// Width (Diameter)
led1p	= 13.5;				// Length plugs
led1t	= led1l+led1p;			// Length total (incl. plugs)
led1m	= led1l+led1t;			// Mounting depth

led2l	=  8.5;				// Length
led2w	=  5.6;				// Width (Diameter)
led2p	= 13.5;				// Length plugs
led2t	= led2l+led2p;			// Length total (incl. plugs)
led2m	= led2l+led2t;			// Mounting depth

// Case dimensions
wo	=  1.6;				// Wall thickness outside
wi	=  0.8;				// Wall thickness inside
wr	=  1.6;				// Wall rounding - Edge radius
cw	= mch+wi+cvw+led2m;		// Width inside		(X)
cl	= sbid+wi+cvw+led1m;// Length inside			(Y)
ch	= 36.0;				// Height inside	(Z)

cvx	= wo+led2m+wi+cvw/2;		// Cuvette holder position	(X)
cvy	= wo+sbid+wi+cvw/2;		//				(Y)
cvz	= wo+ch-ledh;			//				(Z)

// Case - Cover for square cuvette
cctw	=  1.2;				// Thickness wall
ccwi	= cvw+1.0;			// Width inside
cchi	= cvh-wo-ch+15.0;		// Height inside

// Case - Lid
clh	=  2.0;				// Height / Thickness (Z)
clg	=  0.8;				// Guide groove
cle	=  0.2;				// Extra guide groove

// Case - Snapper
csd	=  1.2;				// Depth
csl	=  8.0;				// Length
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

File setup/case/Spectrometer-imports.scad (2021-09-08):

translate([-250,50,0])
rotate ([-90,0,0]){
import("C:/Users/A410882/Downloads/DIY+Spectroscope+with+USB+Webcam+and+Grating (3)/files/Case_Base_Bottom.stl");
}

translate([20,0,0])
rotate ([90,0,0]){
    import("C:/Users/A410882/Downloads/DIY+Spectroscope+with+USB+Webcam+and+Grating (3)/files/Case_Top_Lid.stl");
}

translate([-50,0,50])
rotate ([0,0,0]){
import("C:/Users/A410882/Downloads/Open_Fiber_Spectrometer (4)/files/Spectrometer_final.STL");
}

translate([-100,0,50])
rotate ([0,0,0]){
import("C:/Users/A410882/Downloads/DIY+Spectroscope+with+USB+Webcam+and+Grating (3)/files/Fixture_AUSDOM1080p.stl");
}

translate([-100,0,50])
rotate ([0,0,0]){
import("C:/Users/A410882/Downloads/DIY+Spectroscope+with+USB+Webcam+and+Grating (3)/files/Grating_Holder_Frame.stl");
}

translate([-100,0,50])
rotate ([0,0,0]){
import("C:/Users/A410882/Downloads/DIY+Spectroscope+with+USB+Webcam+and+Grating (3)/files/Slit_Holder_Frame.stl");
}

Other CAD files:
setup/case/3d-printing/Anycubic-Kobra-S1/ACE-Pro-Filament-Guide-and-Drybox/AcePro_Drybox_Filamentguide_v4.3.2_PETG_BL.3mf
setup/case/3d-printing/Anycubic-Kobra-S1/Universal+Anycubic+ACE+Pro+Riser+with+Skadis+Board/The lower Tray - BBL.3mf
setup/case/3d-printing/grating-Spectrometer/grating-Spectrometer-Lightslit-Holder.stl
setup/case/ToslinkConnector.scad
setup/case/3d-printing/Anycubic-Kobra-S1/ACE-Pro-Filament-Guide-and-Drybox/AcePro_Drybox_Filamentguide_v4.3.1_ABS_BL.3mf
setup/case/3d-printing/Anycubic-Kobra-S1/ACE-Pro-Filament-Guide-and-Drybox/Drybox_Middle_v4.3.1.stl
setup/case/3d-printing/Anycubic-Kobra-S1/Short+Universal+Anycubic+ACE+Pro+Riser+with+Skadis/S1C Adapter Right.3mf
setup/case/3d-printing/Anycubic-Kobra-S1/Short+Universal+Anycubic+ACE+Pro+Riser+with+Skadis/The upper Tray - BBL.3mf
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

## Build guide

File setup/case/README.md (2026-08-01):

Banner

# smartPhotometer

## Case

smartPhotometer **cases are designed by OpenSCAD** https://www.openscad.org/ .

OpenSCAD is a software for creating solid 3D CAD models.  
It is free software and available for Linux/UNIX, Windows and Mac OS X.

OpenSCAD is a 3D compiler that reads in a script file that describes the 3D object and renders the 3D model from this script file.  
This provides full control over the 3D modelling process and enables the change of any step in the modelling process **by configurable parameters**.

**3D printing is supported via OpenSCAD STL exports**, the most common file format used for 3D printing.

<table>
<tr>
  <td colspan=2><sub><b>Case</b>
  <td colspan=8><sub>OpenSCAD 3D model (<a href='./smartPhotometer-3d-model.scad'>smartPhotometer-3d-model.scad</a>)
</tr>
<tr>
  <td>
  <td><sub>3D printing
  <td colspan=8><sub>via STL exports
</tr>
<tr>
  <td>
  <td><sub>Filament
  <td colspan=8><sub>Black PLA
</tr>
<tr>
  <td>
  <td><sub>Layer height [mm]
  <td colspan=8><sub>0.2
</tr>
<tr>
  <td rowspan=14>
  <td rowspan=14><sub>STL exports
  <td colspan=4><sub><a href='./3d-printing/smart-RGB-Photometer-Case.stl'>smart-RGB-Photometer-Case.stl</a>
  <td><sub><a href='./3d-printing/smart-UV-Photometer-Case.stl'>smart-UV-Photometer-Case.stl</a>
  <td colspan=2><sub><a href='./3d-printing/smart-IR-Turbidimeter-Case.stl'>smart-IR-Turbidimeter-Case.stl</a>
  <td><sub><a href='./3d-printing/smart-Colorimeter-Case.stl'>smart-Colorimeter-Case.stl</a>
</tr>
<tr>
  <td colspan=8><sub><a href='./3d-printing/smart-Photometer-Case-Lid.stl'>smart-Photometer-Case-Lid.stl</a>
</tr>
<tr>

  <td colspan=8><sub><a href='./3d-printing/smart-Photometer-Cover-for-square-Cuvette.stl'>smart-Photometer-Cover-for-square-Cuvette.stl</a>
</tr>
<tr>
  <td colspan=4><sub><a href='./3d-printing/smart-RGB-Photometer-Cuvette-Holder.stl'>smart-RGB-Photometer-Cuvette-Holder.stl</a>
  <td><sub><a href='./3d-printing/smart-UV-Photometer-Cuvette-Holder.stl'>smart-UV-Photometer-Cuvette-Holder.stl</a>
  <td colspan=2><sub><a href='./3d-printing/smart-IR-Turbidimeter-Cuvette-Holder.stl'>smart-IR-Turbidimeter-Cuvette-Holder.stl</a>
  <td><sub><a href='./3d-printing/smart-Colorimeter-Cuvette-Holder.stl'>smart-Colorimeter-Cuvette-Holder.stl</a>
</tr>
<tr>
  <td colspan=8><sub><a href='./3d-printing/grating-Spectrometer/grating-Spectrometer-Case.stl'>grating-Spectrometer-Case.stl</a>
</tr>
<tr>
  <td colspan=8><sub><a href='./3d-printing/grating-Spectrometer/grating-Spectrometer-Case-Lid.stl'>grating-Spectrometer-Case-Lid.stl</a>
</tr>
<tr>
  <td colspan=8><sub><a href='./3d-printing/grating-Spectrometer/grating-Spectrometer-Lightslit-Holder.stl'>grating-Spectrometer-Lightslit-Holder.stl</a>
</tr>
<tr>
  <td colspan=8><sub><a href='./3d-printing/smart-Spectrometer-Grating-Holder.stl'>smart-Spectrometer-Grating-Holder.stl</a>
</tr>
<tr>
  <td colspan=8><sub><a href='./3d-printing/smart-Spectrometer-Lightslit-Cuvette-Holder.stl'>smart-Spectrometer-Lightslit-Cuvette-Holder.stl</a>
</tr>
<tr>
  <td colspan=8><sub><a href='./3d-printing/smart-Spectrometer-Cover-for-square-Cuvette.stl'>smart-Spectrometer-Cover-for-square-Cuvette.stl</a>
</tr>
<tr>
  <td colspan=8><sub><a href='./3d-printing/smart-Spectrometer-USB-Camera-Holder.stl'>smart-Spectrometer-USB-Camera-Holder.stl</a>
</tr>
<tr>
  <td colspan=8><sub><a href='./3d-printing/smart-Cuvette-Holder-Toslink-Connectors.stl'>smart-Cuvette-Holder-Toslink-Connectors.stl</a>
</tr>
<tr>
  <td colspan=8><sub><a href='./3d-printing/smart-LED-Array-Case-12x12cm.stl'>smart-LED-Array-Case-12x12cm.stl</a>
</tr>
<tr>
  <td colspan=8><sub><a href='./3d-printing/smart-LED-Array-LED-Holder-for-12x12cm-Case.stl'>smart-LED-Array-LED-Holder-for-12x12cm-Case.stl</a>
</tr>
</table>
</br>
<br /><span xmlns:dct="http://purl.org/dc/terms/" property="dct:title">smartPhotometer</span> by <a xmlns:cc="http://creativecommons.org/ns#" href="https://github.com/smartaquametering" property="cc:attributionName" rel="cc:attributionURL">smartAquaMetering</a> is licensed under a <a rel="license" href="http://creativecommons.org/licenses/by-sa/4.0/">Creative Commons Attribution-ShareAlike 4.0 International License</a>.<br />Based on a work at <a xmlns:dct="http://purl.org/dc/terms/" href="https://github.com/smartaquametering/smartPhotometer" rel="dct:source">https://github.com/smartaquametering/smartPhotometer</a>.<br />For permissions beyond the scope of this license see <a xmlns:cc="http://creativecommons.org/ns#" href="https://github.com/smartaquametering/smartPhotometer/blob/main/LICENSE" rel="cc:morePermissions">https://github.com/smartaquametering/smartPhotometer/blob/main/LICENSE</a>.

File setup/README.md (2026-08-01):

Banner

# smartAquaMeter

Easy-to-use OpenSource AquaMeter for measurement of various analytical parameters.
Due to their wide range of application, their reliability and robustness, smartAquaMeters **can be perfectly used as portable analytical instruments for outdoor analytics**.

**Your insurance for secure measurement results.**

## Reducing complexity

Reducing of complexity
- by using **RGB, UV and IR LEDs for the parallel measurement of absorption and nephelometric turbidity** at different wavelengths.
- by the integration of various **digital light sensors and electrochemical sondenxxxxxx orchestrated by simple microcontrollers**.
- by distributing different analysis methods **on multiple meshed smartAquaMeters**.
- by the strict **segregation of data acquisition, transmission, analytics and their visualisation** on different layers and devices.

## Being Smart - The difference

Connect the smartAquaMeter via WiFi to your internal network and orchestrate by using simple web- or MQTT-based APIs.

Networking

Any device (e.g. PC, Laptop, Tablet, smartPhone, ...) with a standard web browser can be used to access a simple web page on the smartAquaMeter.

A Javascript application will start within your browser and is triggering and managing all analytis, evaluation of measured values and their visualisation.

### ESPEasy P2P network example

<table>
<tr>
  <td rowspan=3 valign=top><sub><b>Task</b>
  <td colspan=2><sub><b>Node</b>
  <td rowspan=3 valign=top><sub><b>Device</b>
  <td rowspan=3 valign=top><sub><b>Values</b>
  <td colspan=3><sub><b>Data Acquisition</b>
</tr>
<tr>
  <td rowspan=2><sub><b>ID
  <td rowspan=2><sub><b>Name
  <td colspan=2><sub><b>Controllers
  <td rowspan=2><sub><b>Interval
</tr>
<tr>
  <td><sub><b>ESPEasy P2P Networking
  <td><sub><b>MQTT
</tr>
<tr>
  <td><sub>1
  <td><sub>1
  <td><sub>Pond-Control
  <td><sub><b>smart-Thermometer</b>
  <td><sub>Water-Temperature
  <td><sub>1
  <td><sub>2
  <td><sub>60
</tr>
<tr>
  <td><sub>2
  <td><sub>1
  <td><sub>Pond-Control
  <td><sub><b>smart-pH-Meter</b>
  <td><sub>pH
  <td><sub>1
  <td><sub>2
  <td><sub>60
</tr>
<tr>
  <td><sub>3
  <td><sub>1
  <td><sub>Pond-Control
  <td><sub><b>smart-EC-Meter</b>
  <td><sub>EC
  <td><sub>1
  <td><sub>2
  <td><sub>60
</tr>
<tr>
  <td><sub>4
  <td><sub>1
  <td><sub>Pond-Control
  <td><sub><b>smart-ORP-Meter</b>
  <td><sub>ORP
  <td><sub>1
  <td><sub>2
  <td><sub>60
</tr>
<tr>
  <td><sub>5
  <td><sub>
  <td><sub>
  <td><sub><b></b>
  <td><sub>
  <td><sub>
  <td><sub>
  <td><sub>
</tr>
<tr>
  <td><sub>6
  <td><sub>
  <td><sub>
  <td><sub><b></b>
  <td><sub>
  <td><sub>
  <td><sub>
  <td><sub>
</tr>
<tr>
  <td><sub>7
  <td><sub>
  <td><sub>
  <td><sub><b></b>
  <td><sub>
  <td><sub>
  <td><sub>
  <td><sub>
</tr>
<tr>
  <td><sub>8
  <td><sub>1
  <td><sub>Pond-Control
  <td><sub><b>Barometer</b>
  <td><sub>Air-Pressure</br>Air-Humidity
  <td><sub>1
  <td><sub>2
  <td><sub>60
</tr>
<tr>
  <td><sub>9
  <td><sub>1
  <td><sub>Pond-Control
  <td><sub><b>Thermometer</b>
  <td><sub>Air-Temperature
  <td><sub>1
  <td><sub>2
  <td><sub>60
</tr>
<tr>
  <td><sub>10
  <td><sub>2
  <td><sub>Lab-RGB-Photometer
  <td><sub><b>smart-RGB-Photometer</b>
  <td><sub><var>E<sub>λ</sub></var></br><var>SAC<sub>λ</sub></var></br>FTU
  <td><sub>1
  <td><sub>2
  <td><sub>7
</tr>
<tr>
  <td><sub>11
  <td><sub>3
  <td><sub>Lab-UV-Photometer
  <td><sub><b>smart-UV-Photometer</b>
  <td><sub><var>SAC<sub>λ</sub></var>
  <td><sub>1
  <td><sub>2
  <td><sub>7
</tr>
<tr>
  <td><sub>12
  <td><sub>4
  <td><sub>Lab-Turbidimeter
  <td><sub><b>smart-IR-Turbidimeter</b>
  <td><sub><var>SAC<sub>λ</sub></var></br>FTU
  <td><sub>1
  <td><sub>2
  <td><sub>7
</tr>
<tr>
  <td><sub>13
  <td><sub>5
  <td><sub>Lab-Colorimeter
  <td><sub><b>smart-Colorimeter</b>
  <td><sub>Color index
  <td><sub>1
  <td><sub>2
  <td><sub>7
</tr>
</table>
</br>
<br /><span xmlns:dct="http://purl.org/dc/terms/" property="dct:title">smartPhotometer</span> by <a xmlns:cc="http://creativecommons.org/ns#" href="https://github.com/smartaquametering" property="cc:attributionName" rel="cc:attributionURL">smartAquaMetering</a> is licensed under a <a rel="license" href="http://creativecommons.org/licenses/by-sa/4.0/">Creative Commons Attribution-ShareAlike 4.0 International License</a>.<br />Based on a work at <a xmlns:dct="http://purl.org/dc/terms/" href="https://github.com/smartaquametering/smartPhotometer" rel="dct:source">https://github.com/smartaquametering/smartPhotometer</a>.<br />For permissions beyond the scope of this license see <a xmlns:cc="http://creativecommons.org/ns#" href="https://github.com/smartaquametering/smartPhotometer/blob/main/LICENSE" rel="cc:morePermissions">https://github.com/smartaquametering/smartPhotometer/blob/main/LICENSE</a>.

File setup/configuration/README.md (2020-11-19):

1.  Power on your ESP32 by connecting it via a micro USB-B-cable to your PC
2.  Open WIN 10 WLAN overview and connect with 'TEST-ESP32' SSID
3.  A browser windows will open and you will redirect to the initial ESPEsay Wifi setup page
4.  Connect your new ESPEasy node to your internal WLAN
5.  You will redirect to the new assigned ESPEasy IP address
6.  Document this ESPEasy node IP address and
    consider to assign a static IP for ESP via DHCP/DNS services
7.  Login to ESPEasy WebGUI
8.  Upload the customized smartPhotometer settings file
    /Tools/Settings/Load/
    Select 'config.dat'
    Upload
9.  Upload the customized smartPhotometer rules1 file
    /Tools/Filesystem/File browser/
    Upload
    Select 'rules1.txt'
    Upload
10.  Upload the smartPhotometer web page
    /Tools/Filesystem/File browser/
    Upload
    Select 'photometer.html'
    Upload
11.  Upload the smartPhotometer logo image
    /Tools/Filesystem/File browser/
    Upload
    Select 'logo.png'
    Upload
12.  Upload the smartPhotometer banner image
    /Tools/Filesystem/File browser/
    Upload
    Select 'banner.png'
    Upload
13.  Disable Sleep Mode
    /Config/Sleep Mode
    Sleep awake time: 0
    Sleep time: 0
14.  Modify Rules Engine Settings
    /Tools/System/Advanced/Rules Settings
    Rules: enabled
    Old Engine: enabled
    Tolerant last parameter: enabled
    SendToHTTP wait for ack: disabled
15.  Modify NTP Settings
    /Tools/System/Advanced/NTP Settings
    Use NTP: enabled
    NTP Hostname: to be customized based on your local LAN settings
16. Modify rules DST Settings
    /Tools/System/Advanced/DST Settings
17. Modify Location Settings
    /Tools/System/Advanced/Location Settings
    Timezone Offset (UTC +): to be customized
18. Reboot
    /Tools/System/Reboot

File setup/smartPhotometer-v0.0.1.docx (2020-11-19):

Konzeption und Aufbau eines mobilen und smarten Photometers mit WLAN/ WIFI – Schnittstelle

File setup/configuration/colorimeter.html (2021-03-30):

##### About

×

##### 

##### Firmware build

ESPEasy (mega), ESP_Easy_mega_20201103_custom_ESP32_4M316k

##### Release

##### HTML, CSS, and JavaScript framework

Bootstrap 4 CSS - https://cdn.jsdelivr.net/npm/bootstrap@4.5.3/dist/css/bootstrap.min.css
jQuery - https://cdn.jsdelivr.net/npm/jquery@3.5.1/dist/jquery.min.js
Bootstrap 4 JS bundle - https://cdn.jsdelivr.net/npm/bootstrap@4.5.3/dist/js/bootstrap.bundle.min.js
Bootstrap 4 Select CSS - https://cdn.jsdelivr.net/npm/bootstrap-select@1.13.14/dist/css/bootstrap-select.min.css
Bootstrap 4 Select JS - https://cdn.jsdelivr.net/npm/bootstrap-select@1.13.14/dist/js/bootstrap-select.min.js
Bootstrap 4 Toggle CSS - https://cdn.jsdelivr.net/gh/gitbrent/bootstrap4-toggle@3.6.1/css/bootstrap4-toggle.min.css
Bootstrap 4 Toggle JS - https://cdn.jsdelivr.net/gh/gitbrent/bootstrap4-toggle@3.6.1/js/bootstrap4-toggle.min.js
Bootstrap 4 Tables CSS - https://cdn.jsdelivr.net/npm/bootstrap-table@1.18.0/dist/bootstrap-table.min.css
Bootstrap 4 Tables JS - https://cdn.jsdelivr.net/npm/bootstrap-table@1.18.0/dist/bootstrap-table.min.js
Bootstrap 4 Tables treegrid - https://cdn.jsdelivr.net/npm/bootstrap-table@1.18.0/dist/extensions/treegrid/bootstrap-table-treegrid.min.js
Bootstrap 4 Tables editable - https://cdn.jsdelivr.net/npm/bootstrap-table@1.18.0/dist/extensions/editable/bootstrap-table-editable.min.js
Bootstrap 4 Tables export - https://cdn.jsdelivr.net/npm/bootstrap-table@1.18.0/dist/extensions/export/bootstrap-table-export.min.js
Bootstrap 4 x-editable CSS - https://cdn.jsdelivr.net/gh/Talv/x-editable@develop/dist/bootstrap4-editable/css/bootstrap-editable.css
Bootstrap 4 x-editable JS - https://cdn.jsdelivr.net/gh/Talv/x-editable@develop/dist/bootstrap4-editable/js/bootstrap-editable.min.js
jQuery TimeCircles CSS - https://cdnjs.cloudflare.com/ajax/libs/timecircles/1.5.3/TimeCircles.min.css
jQuery TimeCircles JS - https://cdnjs.cloudflare.com/ajax/libs/timecircles/1.5.3/TimeCircles.min.js
jQuery treegrid CSS - https://cdn.jsdelivr.net/npm/jquery-treegrid@0.3.0/css/jquery.treegrid.css
jQuery treegrid JS - https://cdn.jsdelivr.net/npm/jquery-treegrid@0.3.0/js/jquery.treegrid.min.js
jQuery tableExport - https://cdn.jsdelivr.net/npm/tableexport.jquery.plugin@1.10.21/tableExport.min.js
Font Awesome CSS - https://cdn.jsdelivr.net/npm/@fortawesome/fontawesome-free@5.15.1/css/all.min.css
Font Awesome JS - https://cdn.jsdelivr.net/npm/@fortawesome/fontawesome-free@5.15.1/js/fontawesome.min.js
Google Chart - https://www.gstatic.com/charts/loader.js
Culori color library for JavaScript - https://cdn.jsdelivr.net/npm/culori@0.18.0/build/culori.umd.min.js
smartAquaMetering Colorimeter JS - https://smartaquametering.github.io/assets/js/colorimeter.js
smartAquaMetering Color conversion and Color delta JS - https://smartaquametering.github.io/assets/js/ColorConversion.js
smartAquaMetering Color scales JS - https://smartaquametering.github.io/assets/js/ColorScales.js

##### Support and documentation

GitHub:

##### Development

GitHub:

##### Copyrights

smartColorimeter - by . All Rights Reserved. Licensed under GNU GPL v3 or higher (http://www.gnu.org/licenses/gpl.html).

##### Licenses

All of the source code to this project is available under licenses which are both free (http://www.gnu.org/philosophy/free-sw.html) and open source (http://www.opensource.org/docs/definition.php).
Most of it is available under GNU GPL (http://www.gnu.org/licenses/gpl.html) and MIT License (https://opensource.org/licenses/MIT).

The remainder of the software which is not under the GNU GPL is available under one of a variety of other licenses. Those that require reproduction of the license text in the distribution are given below.
(Note: Your copy of this product may not contain code covered by one or more of the licenses listed here, depending on the exact product and version you choose.)

ESPEasy - Copyright © letscontrolit (https://github.com/letscontrolit/ESPEasy/blob/mega/License.txt). Licensed under GNU GPL v3 or higher (https://github.com/letscontrolit/ESPEasy/blob/mega/License.txt).
Bootstrap - Copyright © 2011-2020 Twitter, Inc (https://github.com/twbs/bootstrap/blob/v4-dev/LICENSE). Licensed under MIT License (https://github.com/twbs/bootstrap/blob/v4-dev/LICENSE).
jQuery - Copyright © OpenJS Foundation and other contributors (https://github.com/jquery/jquery/blob/master/LICENSE.txt). Licensed under MIT License (https://github.com/jquery/jquery/blob/master/LICENSE.txt).
Bootstrap 4 Select - Copyright © 2012-2018 SnapAppointments, LLC (https://github.com/snapappointments/bootstrap-select/blob/v1.14-dev/LICENSE). Licensed under MIT License (https://github.com/snapappointments/bootstrap-select/blob/v1.14-dev/LICENSE).
Bootstrap 4 Toggle - Copyright © 2018 by Brent Ely (https://github.com/gitbrent/bootstrap4-toggle/blob/master/LICENSE). Licensed under MIT License (https://github.com/gitbrent/bootstrap4-toggle/blob/master/LICENSE).
Bootstrap 4 Tables - Copyright © 2012-2019 by Zhixin Wen (https://github.com/wenzhixin/bootstrap-table/blob/master/LICENSE). Licensed under MIT License (https://github.com/wenzhixin/bootstrap-table/blob/master/LICENSE).
Bootstrap 4 x-editable - Copyright © 2012 Vitaliy Potapov (https://github.com/Talv/x-editable/blob/develop/dist/LICENSE-MIT). Licensed under MIT License (https://github.com/Talv/x-editable/blob/develop/dist/LICENSE-MIT).
jQuery TimeCircles - Copyright © 2013 by Wim Barelds (https://github.com/wimbarelds/TimeCircles/blob/master/MIT.txt). Licensed under MIT License (https://github.com/wimbarelds/TimeCircles/blob/master/MIT.txt).
jQuery treegrid - Copyright © 2013 by Maksym Pomazan (https://github.com/maxazan/jquery-treegrid/blob/master/LICENSE). Licensed under MIT License (https://github.com/maxazan/jquery-treegrid/blob/master/LICENSE).
jQuery tableExport - Copyright © 2015-2020 by hhurz (https://github.com/hhurz/tableExport.jquery.plugin/blob/master/LICENSE). Licensed under MIT License (https://github.com/hhurz/tableExport.jquery.plugin/blob/master/LICENSE).
Font Awesome - by Font Awesome (https://github.com/FortAwesome/Font-Awesome/blob/master/LICENSE.txt).
Google Chart - Copyright © Google Inc (https://github.com/GoogleWebComponents/google-chart/blob/master/LICENSE). Licensed under Apache License 2.0 (https://github.com/GoogleWebComponents/google-chart/blob/master/LICENSE).
Color converting functions - Copyright © 2001-2021 by Bruce Justin Lindbloom (http://www.brucelindbloom.com/index.html?ColorCalculator.html).
Color delta functions - Copyright © 2001-2021 by Bruce Justin Lindbloom (http://www.brucelindbloom.com/index.html?ColorDifferenceCalc.html).
Culori color library for JavaScript - Copyright © 2018 by Dan Burzo (https://github.com/Evercoder/culori/blob/master/LICENSE). Licensed under MIT License (https://github.com/Evercoder/culori/blob/master/LICENSE).

Close

##### Help

×

##### 

##### Legend

λ

Wavelength [nm]

Bo

Beam (measuring) angle [o] 180 o: Transmitted light measurement (Absorbance) 90 o: Nephelometric turbidity (scattered light) measurement

I0

Intensity of incident light [lux]

IT

Intensity of transmitted light [lux]

T = IT / I0

Transmission Energy passing through Range: 0.0 - 1.0

A = 1 - T

Absorption Energy lost

Eλ = - log ( T ) = ελ * c * d

Absorbance Attenuation Lambert-Beer law Optimum range: 0.1 – 1.0

SACλ = Eλ / d * 100

Spectral Absorption Coefficient [m⁻¹]

c = Eλ / ( ελ * d ) = Eλ * F

Concentration of absorbing substance in the liquid [mol/l]

F = 1 / ( ελ * d )

Factor Test specific

ελ

Molar decadic extinction coefficient [l/mol/cm]

d

Thickness of the solution layer [cm]

Turbidity

Opacity, clouding, haze

FNU

Formazine Nephelometric Unit

NTU

Nephelometric Turbidity Unit

FAU

Formazine Attenuation Unit

##### Measurement methods

Photometry

Absorbance measurement (transmitted light or absorption measurement) Recommended measuring range: 40–4000 FAU (DIN EN ISO 7027) Light source and detector are located on the same axis (180° angle). The reduced light intensity which remains after passing through the sample is measured

Nephelometry

Scattered light measurement Recommended measuring range: 0–40 FNU (DIN EN ISO 7027) Light source and detector are oriented at an angle of 90° relative to each other

Close

#### Status

Source white

Reference white

Adaptation method

RGB model

Color scale

Your browser does not support the HTML canvas tag.

#### Readings

Reset

#### Protocol

Reset

#### Logging

Enable Reset Disable

by

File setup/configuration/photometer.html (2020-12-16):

##### About

×

##### 

##### Firmware build

ESPEasy (mega), ESP_Easy_mega_20201103_custom_ESP32_4M316k

##### Release

##### HTML, CSS, and JavaScript framework

Bootstrap 4 CSS - https://cdn.jsdelivr.net/npm/bootstrap@4.5.3/dist/css/bootstrap.min.css
jQuery - https://cdn.jsdelivr.net/npm/jquery@3.5.1/dist/jquery.min.js
Bootstrap 4 JS bundle - https://cdn.jsdelivr.net/npm/bootstrap@4.5.3/dist/js/bootstrap.bundle.min.js
Bootstrap 4 Toggle CSS - https://cdn.jsdelivr.net/gh/gitbrent/bootstrap4-toggle@3.6.1/css/bootstrap4-toggle.min.css
Bootstrap 4 Toggle JS - https://cdn.jsdelivr.net/gh/gitbrent/bootstrap4-toggle@3.6.1/js/bootstrap4-toggle.min.js
Bootstrap 4 Tables CSS - https://cdn.jsdelivr.net/npm/bootstrap-table@1.18.0/dist/bootstrap-table.min.css
Bootstrap 4 Tables JS - https://cdn.jsdelivr.net/npm/bootstrap-table@1.18.0/dist/bootstrap-table.min.js
Bootstrap 4 Tables treegrid - https://cdn.jsdelivr.net/npm/bootstrap-table@1.18.0/dist/extensions/treegrid/bootstrap-table-treegrid.min.js
Bootstrap 4 Tables editable - https://cdn.jsdelivr.net/npm/bootstrap-table@1.18.0/dist/extensions/editable/bootstrap-table-editable.min.js
Bootstrap 4 Tables export - https://cdn.jsdelivr.net/npm/bootstrap-table@1.18.0/dist/extensions/export/bootstrap-table-export.min.js
Bootstrap 4 x-editable CSS - https://cdn.jsdelivr.net/gh/Talv/x-editable@develop/dist/bootstrap4-editable/css/bootstrap-editable.css
Bootstrap 4 x-editable JS - https://cdn.jsdelivr.net/gh/Talv/x-editable@develop/dist/bootstrap4-editable/js/bootstrap-editable.min.js
jQuery TimeCircles CSS - https://cdnjs.cloudflare.com/ajax/libs/timecircles/1.5.3/TimeCircles.min.css
jQuery TimeCircles JS - https://cdnjs.cloudflare.com/ajax/libs/timecircles/1.5.3/TimeCircles.min.js
jQuery treegrid CSS - https://cdn.jsdelivr.net/npm/jquery-treegrid@0.3.0/css/jquery.treegrid.css
jQuery treegrid JS - https://cdn.jsdelivr.net/npm/jquery-treegrid@0.3.0/js/jquery.treegrid.min.js
jQuery tableExport - https://cdn.jsdelivr.net/npm/tableexport.jquery.plugin@1.10.21/tableExport.min.js
Font Awesome CSS - https://cdn.jsdelivr.net/npm/@fortawesome/fontawesome-free@5.15.1/css/all.min.css
Font Awesome JS - https://cdn.jsdelivr.net/npm/@fortawesome/fontawesome-free@5.15.1/js/fontawesome.min.js

##### Support and documentation

GitHub:

##### Development

GitHub:

##### Copyrights

smartPhotometer - by . All Rights Reserved. Licensed under GNU GPL v3 or higher (http://www.gnu.org/licenses/gpl.html).

##### Licenses

All of the source code to this project is available under licenses which are both free (http://www.gnu.org/philosophy/free-sw.html) and open source (http://www.opensource.org/docs/definition.php).
Most of it is available under GNU GPL (http://www.gnu.org/licenses/gpl.html) and MIT License (https://opensource.org/licenses/MIT).

The remainder of the software which is not under the GNU GPL is available under one of a variety of other licenses. Those that require reproduction of the license text in the distribution are given below.
(Note: Your copy of this product may not contain code covered by one or more of the licenses listed here, depending on the exact product and version you choose.)

ESPEasy - Copyright © letscontrolit (https://github.com/letscontrolit/ESPEasy/blob/mega/License.txt). Licensed under GNU GPL v3 or higher (https://github.com/letscontrolit/ESPEasy/blob/mega/License.txt).
Bootstrap - Copyright © 2011-2020 Twitter, Inc (https://github.com/twbs/bootstrap/blob/v4-dev/LICENSE). Licensed under MIT License (https://github.com/twbs/bootstrap/blob/v4-dev/LICENSE).
jQuery - Copyright © OpenJS Foundation and other contributors (https://github.com/jquery/jquery/blob/master/LICENSE.txt). Licensed under MIT License (https://github.com/jquery/jquery/blob/master/LICENSE.txt).
Bootstrap 4 Toggle - Copyright © 2018 by Brent Ely (https://github.com/gitbrent/bootstrap4-toggle/blob/master/LICENSE). Licensed under MIT License (https://github.com/gitbrent/bootstrap4-toggle/blob/master/LICENSE).
Bootstrap 4 Tables - Copyright © 2012-2019 by Zhixin Wen (https://github.com/wenzhixin/bootstrap-table/blob/master/LICENSE). Licensed under MIT License (https://github.com/wenzhixin/bootstrap-table/blob/master/LICENSE).
jQuery TimeCircles - Copyright © 2013 by Wim Barelds (https://github.com/wimbarelds/TimeCircles/blob/master/MIT.txt). Licensed under MIT License (https://github.com/wimbarelds/TimeCircles/blob/master/MIT.txt).
jQuery treegrid - Copyright © 2013 by Maksym Pomazan (https://github.com/maxazan/jquery-treegrid/blob/master/LICENSE). Licensed under MIT License (https://github.com/maxazan/jquery-treegrid/blob/master/LICENSE).
jQuery tableExport - Copyright © 2015-2020 by hhurz (https://github.com/hhurz/tableExport.jquery.plugin/blob/master/LICENSE). Licensed under MIT License (https://github.com/hhurz/tableExport.jquery.plugin/blob/master/LICENSE).
Font Awesome - by Font Awesome (https://github.com/FortAwesome/Font-Awesome/blob/master/LICENSE.txt).

Close

##### Help

×

##### 

##### Legend

λ

Wavelength [nm]

Bo

Beam (measuring) angle [o] 180 o: Transmitted light measurement (Absorbance) 90 o: Nephelometric turbidity (scattered light) measurement

I0

Intensity of incident light [lux]

IT

Intensity of transmitted light [lux]

T = IT / I0

Transmission Energy passing through Range: 0.0 - 1.0

A = 1 - T

Absorption Energy lost

Eλ = - log ( T ) = ελ * c * d

Absorbance Attenuation Lambert-Beer law Optimum range: 0.1 – 1.0

SACλ = Eλ / d * 100

Spectral Absorption Coefficient [m⁻¹]

c = Eλ / ( ελ * d ) = Eλ * F

Concentration of absorbing substance in the liquid [mol/l]

F = 1 / ( ελ * d )

Factor Test specific

ελ

Molar decadic extinction coefficient [l/mol/cm]

d

Thickness of the solution layer [cm]

Turbidity

Opacity, clouding, haze

FNU

Formazine Nephelometric Unit

NTU

Nephelometric Turbidity Unit

FAU

Formazine Attenuation Unit

##### Measurement methods

Photometry

Absorbance measurement (transmitted light or absorption measurement) Recommended measuring range: 40–4000 FAU (DIN EN ISO 7027) Light source and detector are located on the same axis (180° angle). The reduced light intensity which remains after passing through the sample is measured

Nephelometry

Scattered light measurement Recommended measuring range: 0–40 FNU (DIN EN ISO 7027) Light source and detector are oriented at an angle of 90° relative to each other

Close

#### Status

#### Readings

Reset

#### Protocol

Reset

#### Logging

Enable Reset Disable

by

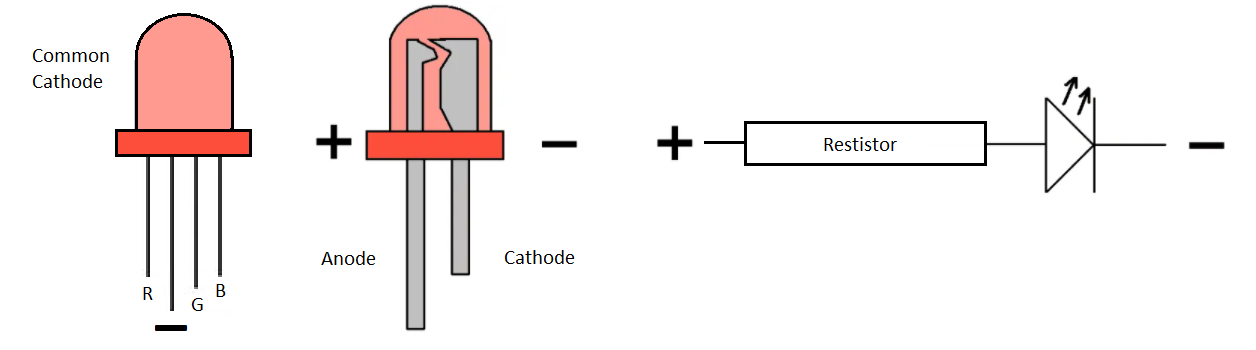
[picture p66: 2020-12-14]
assets/wiring-leds.png

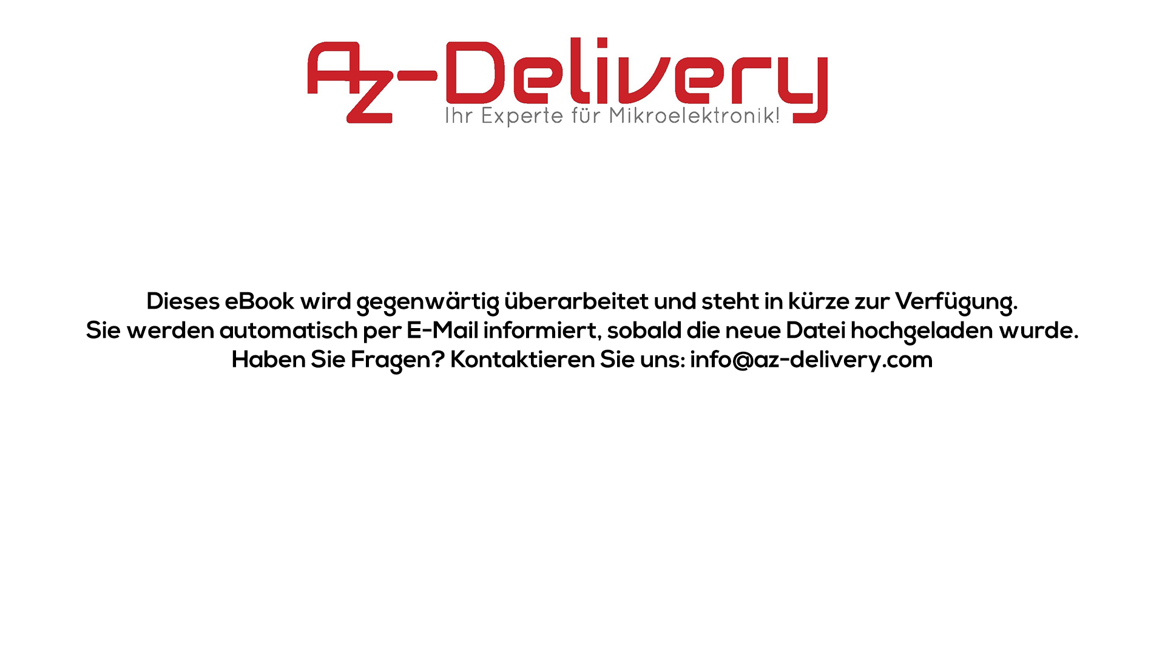
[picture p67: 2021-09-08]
docs-AZ-Delivery/DEU - eBook ist im Aufbau (2).png

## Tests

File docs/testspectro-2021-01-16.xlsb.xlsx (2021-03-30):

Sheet: Sensor
Reference White | D65 | XW |  |  | 0.95047 |  | https://en.wikipedia.org/wiki/Standard_illuminant
 |  | YW |  |  | 1 |  | http://www.brucelindbloom.com/index.html?WorkingSpaceInfo.html
 |  | ZW |  |  | 1.08883 |  | https://github.com/ha5dzs/colour_sensor_primary_calculator/blob/master/primaries.txt
RGB system | Sensor | xr |  |  | 0.582692
 |  | yr |  |  | 0.382919
 |  | xg |  |  | 0.283233
 |  | yg |  |  | 0.52567
 |  | xb |  |  | 0.14456
 |  | yb |  |  | 0.134175
RGB/XYZ Matrices |  |  |  | | | 0.582692 | 0.283233 | 0.14456
 |  |  | = | | | 0.283233 | 0.52567 | 0.134175
 |  |  |  | | | 0.134075 | 0.191097 | 0.721265
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

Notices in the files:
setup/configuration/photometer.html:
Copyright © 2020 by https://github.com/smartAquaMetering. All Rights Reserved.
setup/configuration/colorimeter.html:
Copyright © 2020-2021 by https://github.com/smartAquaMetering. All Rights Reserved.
